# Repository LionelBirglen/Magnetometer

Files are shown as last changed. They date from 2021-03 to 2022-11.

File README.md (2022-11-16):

# Open-Source Magnetometer

This is a repository for an open-source magnetometer.

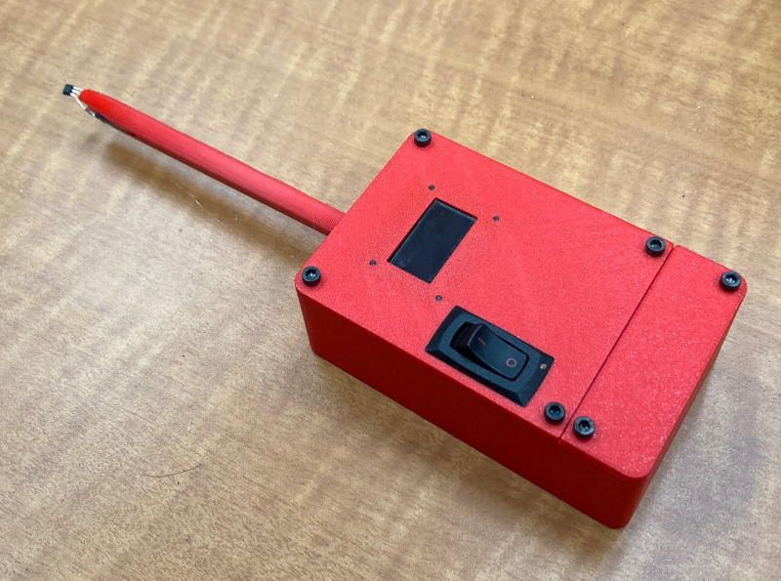
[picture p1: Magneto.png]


For instructions, see YouTube video: 

Arduino Program:
- Magnetometre.ino

CAD Files:
- Magnetometre.igs
- Magnetometre.stp 

To modify as you please. All 3D printed parts are in the file.

3D Printer Files:
- Magnetometre_MainBox.stl
- Magnetometre_BatteryLid.stl
- Magnetometre_MainLid.stl
- Magnetometre_SensorStrainRelief.stl
- Magnetometre_SensorTube.stl
- Magnetometre_FTDICap.stl

Print one of each in your choice of filament, PLA or PETG work fine.

Bill of Materials:
- Magnetometre_BOM.ods

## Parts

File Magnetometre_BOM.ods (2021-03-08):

OPEN-SOURCE MAGNETOMETER
by Lionel Birglen, 2021
GNU General Public License v3.0
Bill of Materials
Name | Supplier | Quantity | Price | Link | Comment
3D Printed Parts
Main Box | PYO | 1 |  |  | 54352 mm3, print your own (PYO)
Main Cover | PYO | 1 |  |  | 9893 mm3
Battery Lid | PYO | 1 |  |  | 5086 mm3
Sensor Tube | PYO | 1 |  |  | 4121 mm3
Sensor Strain Relief | PYO | 1 |  |  | 586 mm3
 |  |  | ca. CAD 0.50 |  | Total = approx. 27m of filaments (82g), no support required but a brim might help with bed adhesion particularly the tube
 |  |  |  |  | cost is estimated at CAD 30$ per kg
Electronics
Arduino Mini Pro 5V version | Arduino | 1 | CAD 12.99 | https://www.robotshop.com/ca/en/arduino-pro-mini-328-5v-16mhz.html | Needs a FTDI programmer if you do not have one already
OR Arduino Nano Every with headers | Arduino | 1 | CAD 17.40 | https://www.robotshop.com/ca/en/arduino-nano-every-microcontroller-with-headers.html
0.96” OLED Display | Adafruit | 1 | USD 17.50 | https://www.adafruit.com/product/326 | Needs to be 5V tolerant
OR 0.95" RGB OLED Display | Adafruit | 1 | CAD 15.39 | https://www.robotshop.com/ca/en/095-rgb-oled-display.html
Three Conductor Cable | Surplus | 1 |  |  | Length: 150mm min, 4 conductor ok too (more common)
OR Three Conductor Cable | Digikey | 1 | CAD 3.30 | https://www.digikey.ca/en/products/detail/30-00371/T1276-1-ND/5270238
Female-Female Jumper cable | Robotshop | 7 | CAD 5.27 | https://www.robotshop.com/ca/en/sfe-170mm-ff-premium-jumper-wires.html | Length: 80mm, not necessary if you solder the pins, one pack is enough
9V Battery Snap | Robotshop | 1 | CAD 1.23 | https://www.robotshop.com/ca/en/9v-battery-bh-06.html | Length: 10cm+ recommended
Straight Female Header | Robotshop | 24 | CAD 0.45 | https://www.robotshop.com/ca/en/straight-female-headers.html | 2x12 for the Arduino
Straight Male Header | Adafruit | 60 | USD 4.95 | https://www.adafruit.com/product/392 | 0.1in pitch, one pack is enough
Right Angle Male Header | Robotshop | 6 | CAD 0.63 | https://www.robotshop.com/ca/en/break-away-header-right-angle.html | 0.1in pitch, one set is enough
Power Switch | Surplus | 1 |  |  | Needs one small wire piece to connect to the arduino (approx. 8cm), cut it from a jumper cable if you don’t have one
OR SPST Rocker Switch | Digikey | 1 | CAD 1.44 | https://www.digikey.ca/en/products/detail/e-switch/R4ABLKREDFF0/1805260 | Should match the hole in the main lid but I did not try it
Prototype board | Surplus | 1 |  |  | Surplus store, 45mm x 45 mm, 0.1in pitch
OR Adafruit Perma-Proto Quarter Size | Adafruit | 1 | USD 2.95 | https://www.adafruit.com/product/1608 | Screw holes available for this board in the main box
SS49E Hall Effect Sensor | Digikey | 1 | CAD 3.04 | https://www.digikey.ca/en/products/detail/honeywell-sensing-and-productivity-solutions/SS49E/701361 | any 5V linear analog output hall sensor should be fine but not latching ones
1x1 Crimp Housing | Pololu | 5 | USD 1.29 | https://www.pololu.com/product/1900 | Not necessary if you solder the pins, one pack is enough
1x3 Crimp Housing | Pololu | 1 | USD 1.69 | https://www.pololu.com/product/1902 | Can be replaced by a 1x3 female header and soldered
Female Crimp Pins for 0.1" Housings | Pololu | 8 | USD 5.95 | https://www.pololu.com/product/1930 | Not necessary if you solder the pins, one pack is enough
Hardware
M3 Screws | Surplus | 8 |  |  | For the lids and the sensor strain relief, any length between 5 to 12 mm is ok, ideally round headed for aesthetics
M3 Screws | Surplus | 4 |  |  | For the soldering board, any length between 3 to 5 mm, washers may be useful depending on your protoboard
M2 Screws | Surplus | 4 |  |  | Length 3mm (more is ok but they will stick out)
 |  | APPROX TOTAL | CAD 70.50
 |  |  | USD 54.25
Required Tools
Soldering Iron
Solder
Wire stripper
Needle nose plier or crimping tool
Screwdriver or Allen key for the screws
9V Battery
Optional: hot glue or better, silastic / neutral cure silicon rubber

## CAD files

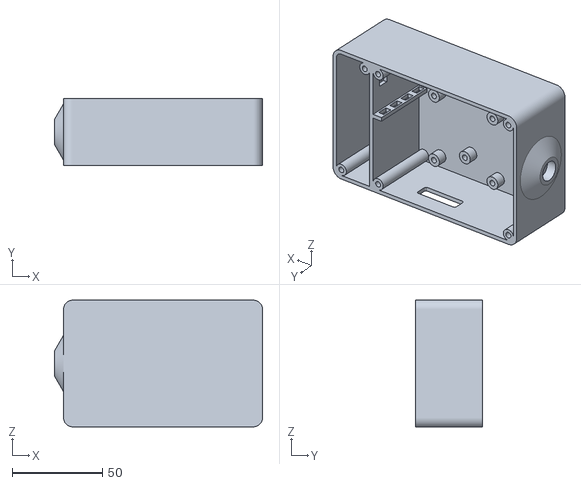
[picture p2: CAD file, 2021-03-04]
Magnetometre_MainBox.stl
115.0 x 37.0 x 70.0

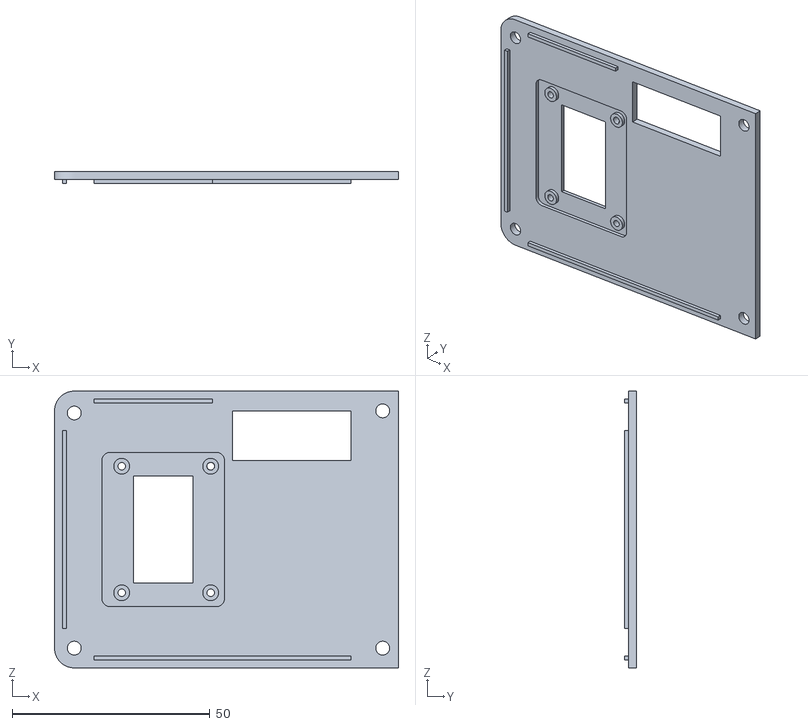
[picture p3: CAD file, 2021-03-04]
Magnetometre_MainLid.stl
87.0 x 3.00 x 70.0

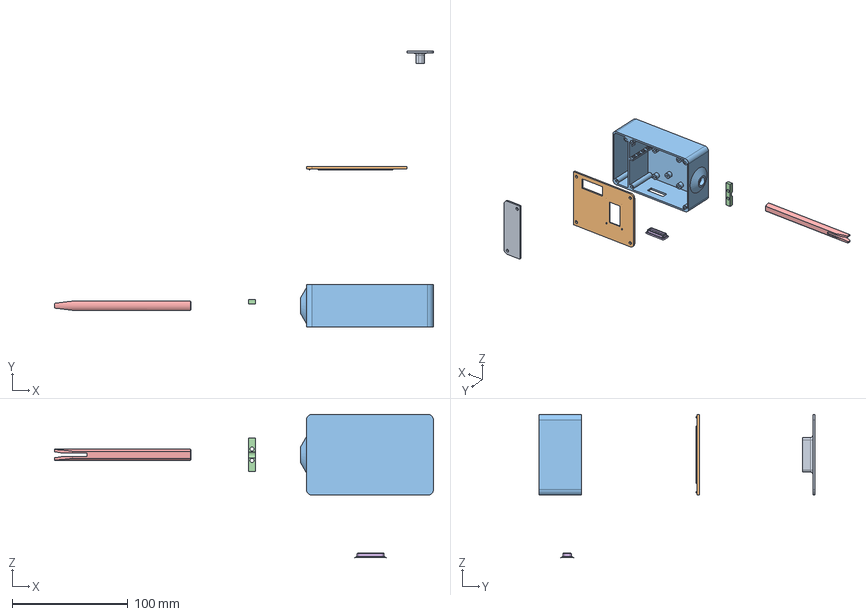
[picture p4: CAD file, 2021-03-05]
Magnetometre.stp
328.0 x 239.0 x 124.0 mm

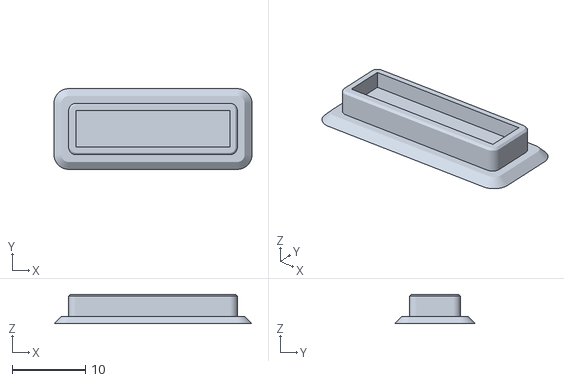
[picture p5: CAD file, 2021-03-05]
Magnetometre_FTDICap.stl
27.0 x 11.0 x 4.00

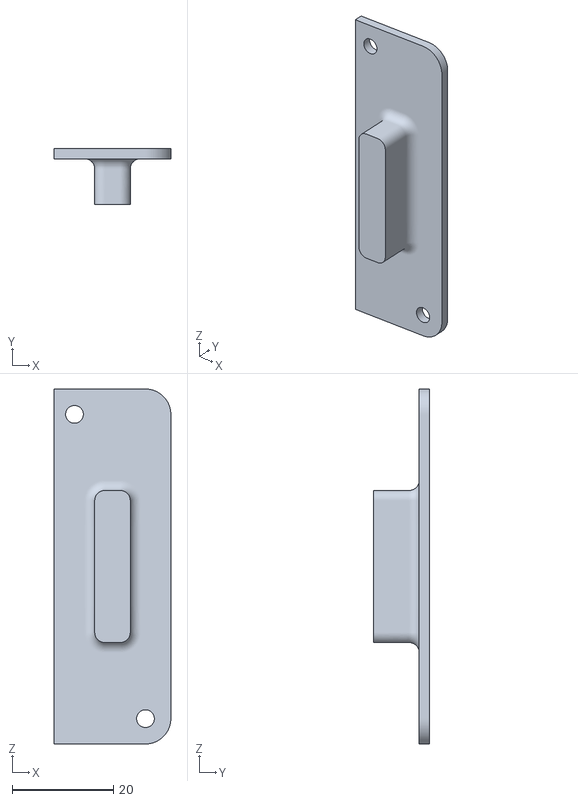
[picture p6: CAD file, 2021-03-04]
Magnetometre_BatteryLid.stl
23.0 x 11.0 x 70.0

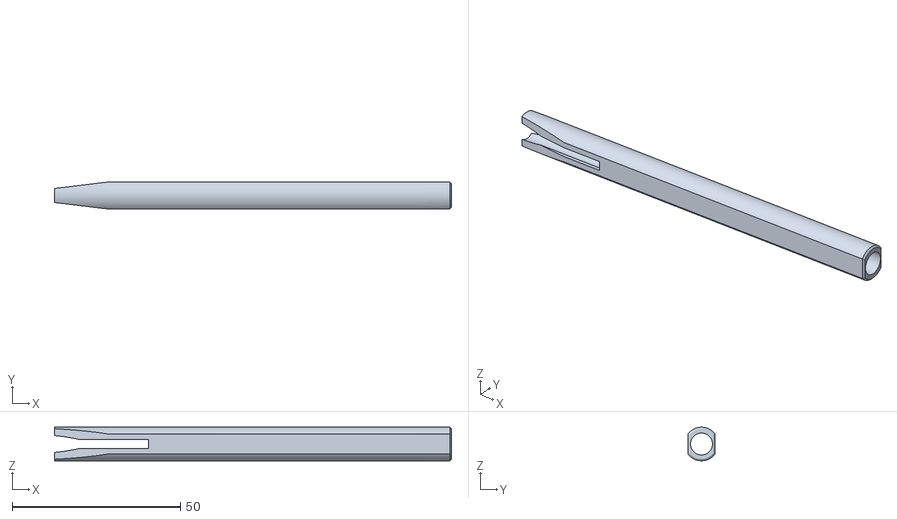
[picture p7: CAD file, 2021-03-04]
Magnetometre_SensorTube.stl
118.0 x 8.00 x 10.0

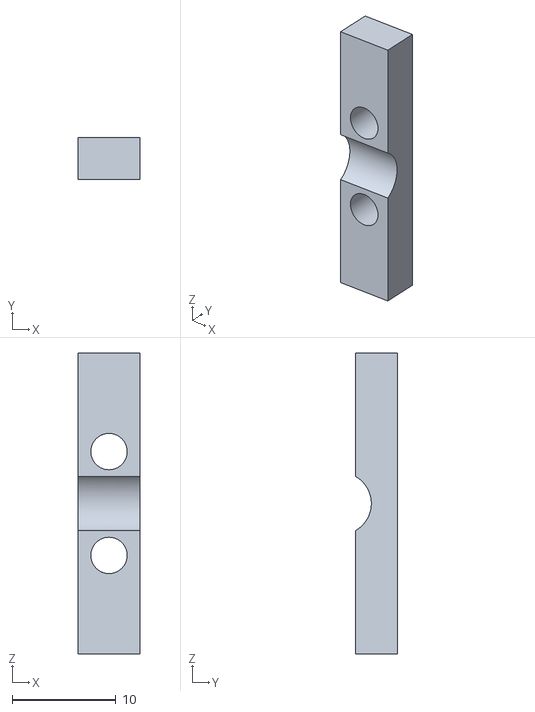
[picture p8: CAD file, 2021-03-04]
Magnetometre_SensorStrainRelief.stl
6.00 x 4.00 x 29.0

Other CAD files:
Magnetometre.igs

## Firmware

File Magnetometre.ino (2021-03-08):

/*
 * Open Source Magnetometer Arduino Code
 * based on Adafruit SSD1306 example program
 * 
 * by Lionel Birglen
 * Polytechnique Montreal
 * March 2021
*/

#include <SPI.h>
#include <Wire.h>
#include <Adafruit_GFX.h>
#include <Adafruit_SSD1306.h>

#define SCREEN_WIDTH 128 // OLED display width, in pixels
#define SCREEN_HEIGHT 64 // OLED display height, in pixels

// Declaration for SSD1306 display connected using software SPI (default case):
#define OLED_MOSI   9
#define OLED_CLK   10
#define OLED_DC    11
#define OLED_CS    12
#define OLED_RESET 13
Adafruit_SSD1306 display(SCREEN_WIDTH, SCREEN_HEIGHT,
  OLED_MOSI, OLED_CLK, OLED_DC, OLED_RESET, OLED_CS);

//Custom variables for magnetometer
int compte=30;
float zero;
int calibration=0;

float mini=0.87; //Minimal voltage output by the sensor, adjusted after experimenting
float maxi=4.20; //Maximal voltage output by the sensor, adjusted after experimenting
float gain=0.0014; //Gain of SS49E sensor : 1.4mV/Gauss


void setup() {
  //Initialize serial communication
  Serial.begin(9600);

  // SSD1306_SWITCHCAPVCC = generate display voltage from 3.3V internally
  if(!display.begin(SSD1306_SWITCHCAPVCC)) {
    Serial.println(F("SSD1306 allocation failed"));
    for(;;); // Don't proceed, loop forever
  }

  // Clear the buffer
  display.clearDisplay();

  //Display that calibration is running
  display.setCursor(0,0); 
  display.setTextSize(1); 
  display.setTextColor(SSD1306_WHITE);
  display.println("Calibration...");

  //read 30 data points to compute the zero G offset, sensor must be away from magnetic sources
  calibration=analogRead(A0);
  for (int i = 1; i < compte; i++) {
    calibration=calibration+analogRead(A0);
    delay(2);
  }
  Serial.println(calibration);
  display.print("Zero = ");
  display.println(calibration);
  display.display();

  //Wait 2 seconds
  delay(2000);
}


void loop() {
  int capteur;
  
  //Read the sensor
  capteur=analogRead(A0);
  
  //Read the sensor "compte-1" more times
  for (int i = 1; i < compte; i++) {
      capteur=capteur+analogRead(A0);
      delay(2);
    }
  
  //Average the values read both before and after calibration is taken into account
  float tension=capteur*(5.0/1023.0)/compte;
  float mesure=(capteur-calibration)*(5.0/1023.0)/compte;

  //Clear and setup the display
  display.clearDisplay(); 
  display.setCursor(0,0); 
  display.setTextSize(1);
  display.setTextColor(SSD1306_WHITE);
  display.print(tension);
  display.println("V");
  display.setTextSize(2);
  
  //Voltages can be below or above calibration value depending if a north or south pole is measured
  if (mesure>0) {
    display.print("+");
  }
  else {
    display.print("-");
  }
  //Display the Gauss value
  display.print(abs(mesure)/gain,1);
  display.println("G");

  //Warn if saturation is reached, displayed value is unreliable
  if (tension<mini || tension>maxi)  {
    display.print("SATURATION");
  }

  //Display everything and wait 20ms
  display.display();
  delay(20); 
}
